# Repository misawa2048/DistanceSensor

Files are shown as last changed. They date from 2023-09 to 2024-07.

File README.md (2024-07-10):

# Open Distance Sensor 
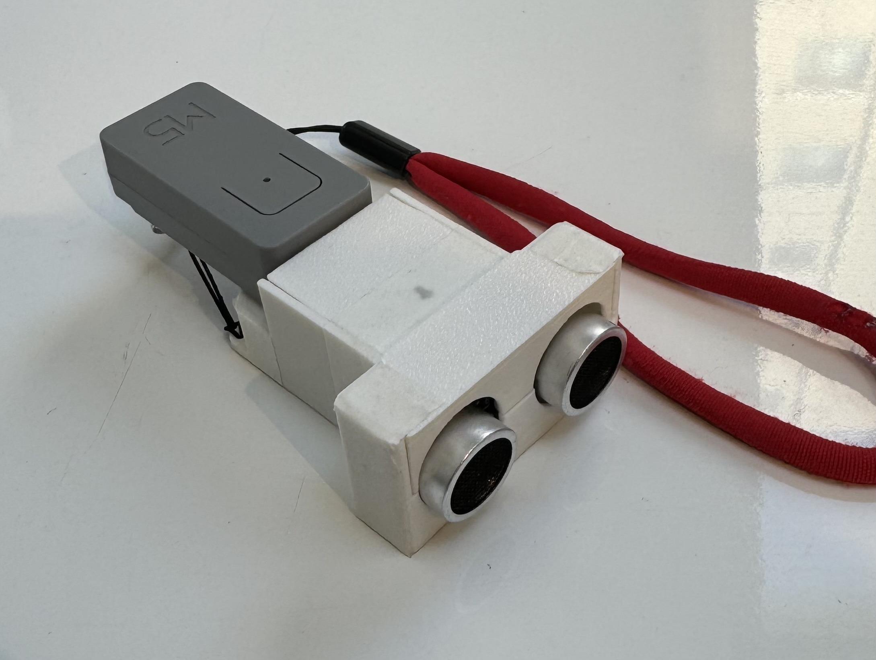
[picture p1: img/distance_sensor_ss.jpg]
  
Open DistanceSensorは、広く一般に流通しているパーツを使用して構成された超音波距離センサーです。 
最大4メートル前方の障害物を認識し、振動の間隔で距離をユーザーに伝えます。  
オープンソースですので、ここにあるデータを用いてどなたでも作成・ご活用いただけます。  

Open DistanceSensor is an ultrasonic distance sensor composed of widely available parts.  
It recognizes obstacles up to 4 meters ahead and tells the user the distance in terms of vibration intervals.  
Open source: Anyone can build and utilize it using the data available here.  

Distance sensor for the visually impaired  
https://youtube.com/shorts/7CfSE-uf2CA?si=v9oYDg3hjXETH1KF  
## Hardware
### PCB  
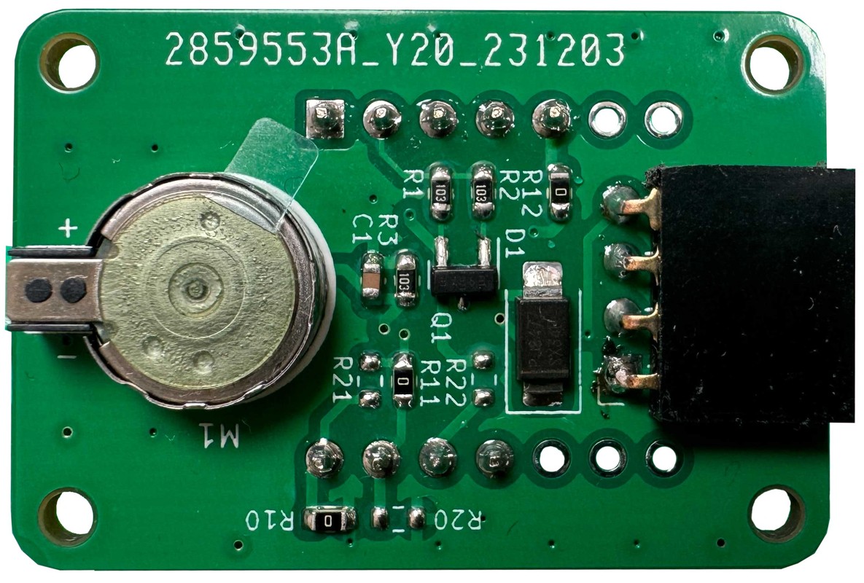
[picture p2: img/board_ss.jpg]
Printed circuit board
  

### STL
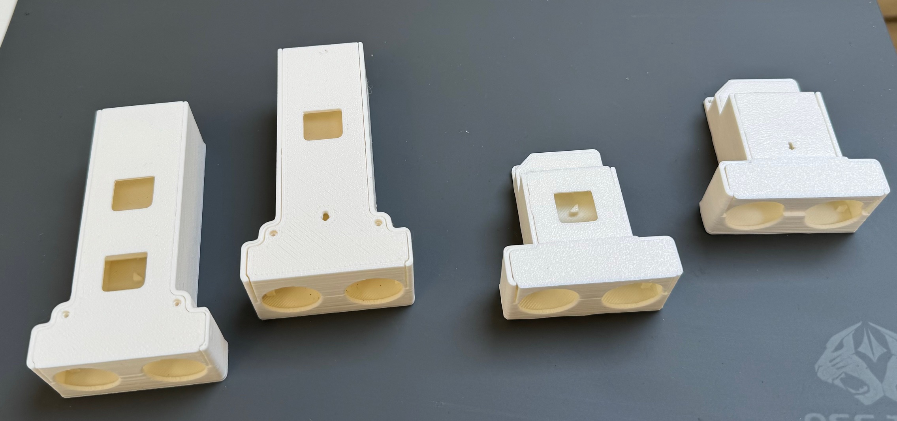
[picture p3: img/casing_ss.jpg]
3D print model
  

### pin asign  
XIAO_RP2040 (front side of mounting)  
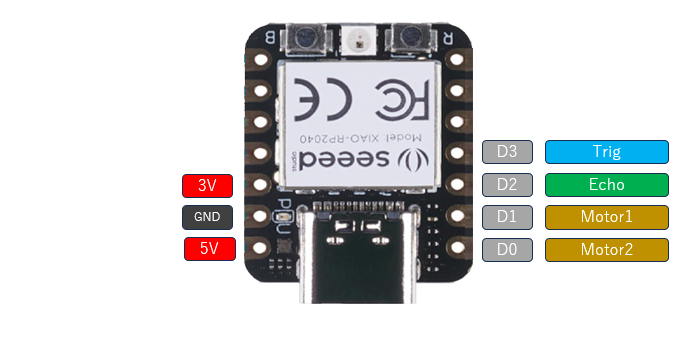
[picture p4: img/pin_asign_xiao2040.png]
pin asign
   
XIAO_RP2040 (front side of mounting)  
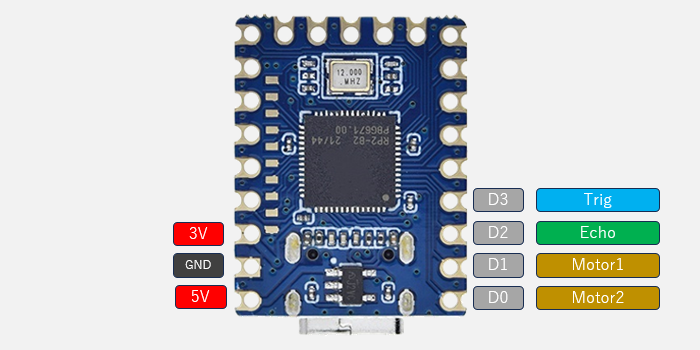
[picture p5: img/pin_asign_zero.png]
pin asign
   
ATOM_S3LITE (back side of mounting)    
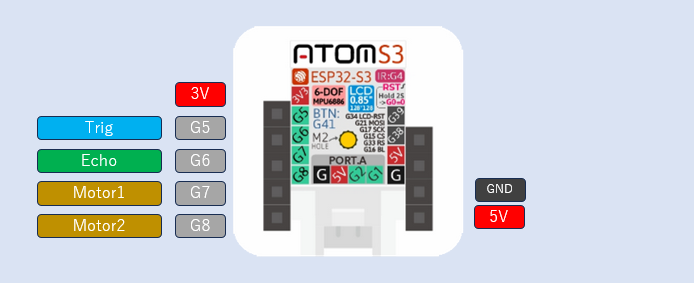
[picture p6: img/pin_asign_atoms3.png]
pin asign
   
 
## Software
Arduino IDE  
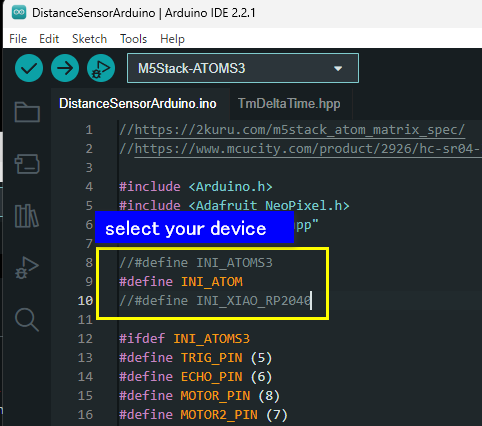
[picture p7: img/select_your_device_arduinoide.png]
select your device
  
PlatformIO  
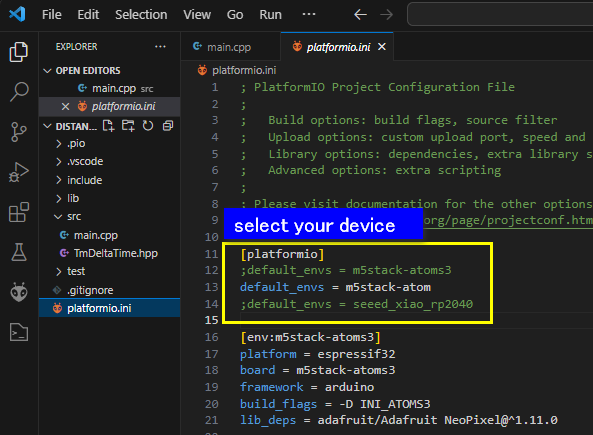
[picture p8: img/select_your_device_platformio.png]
select your device
  

### prototypes  
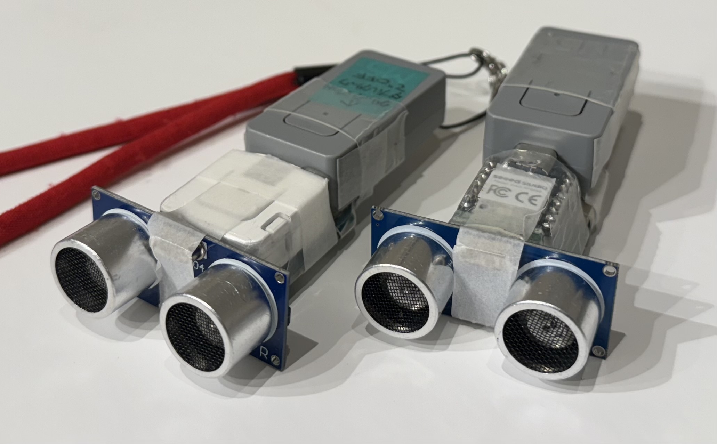
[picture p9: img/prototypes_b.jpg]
prototype
  
prototype  

## Support
こちらのプロジェクトは  
令和5年度 競争力強化支援事業（ソフトウェア開発費助成）として  
品川区より支援を受けております（支援金額:￥273000）。  

## Links  
[board manager settings](https://2kuru.com/m5stack_atom_matrix_spec/)  
[About distance sensor](https://www.mcucity.com/product/2926/hc-sr04-3-3v-5v-ultrasonic-distance-measuring-sensor-module-trig-echo-uarttx-rx-i2csdascl)

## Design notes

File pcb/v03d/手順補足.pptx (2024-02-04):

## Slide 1

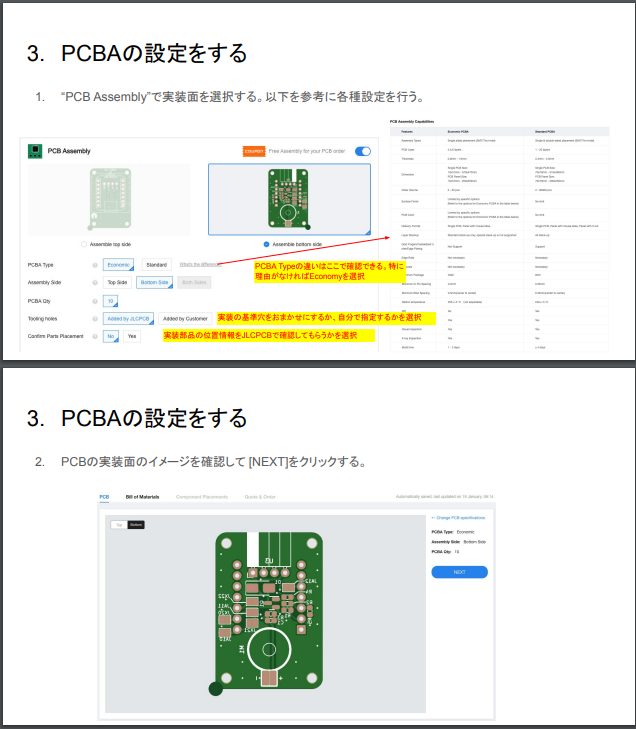
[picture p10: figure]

Calculated Priceの下にある[NEXT]を押す
を追加

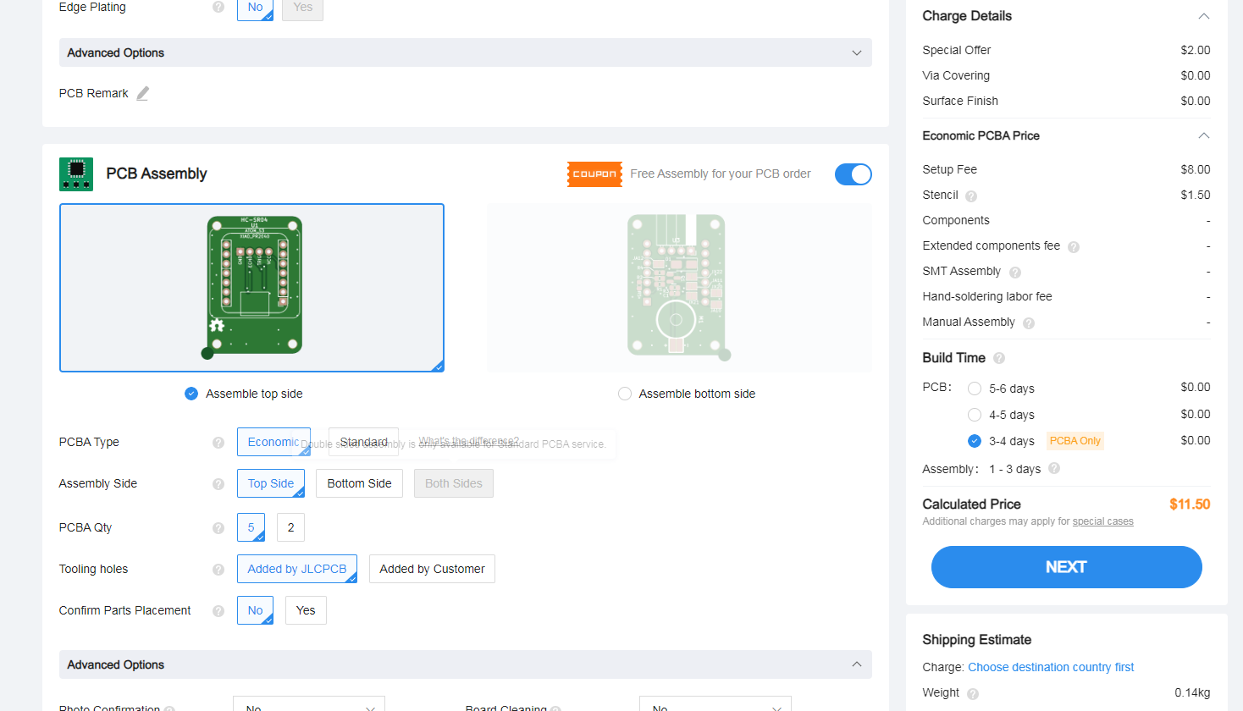
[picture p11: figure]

間に挟む

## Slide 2

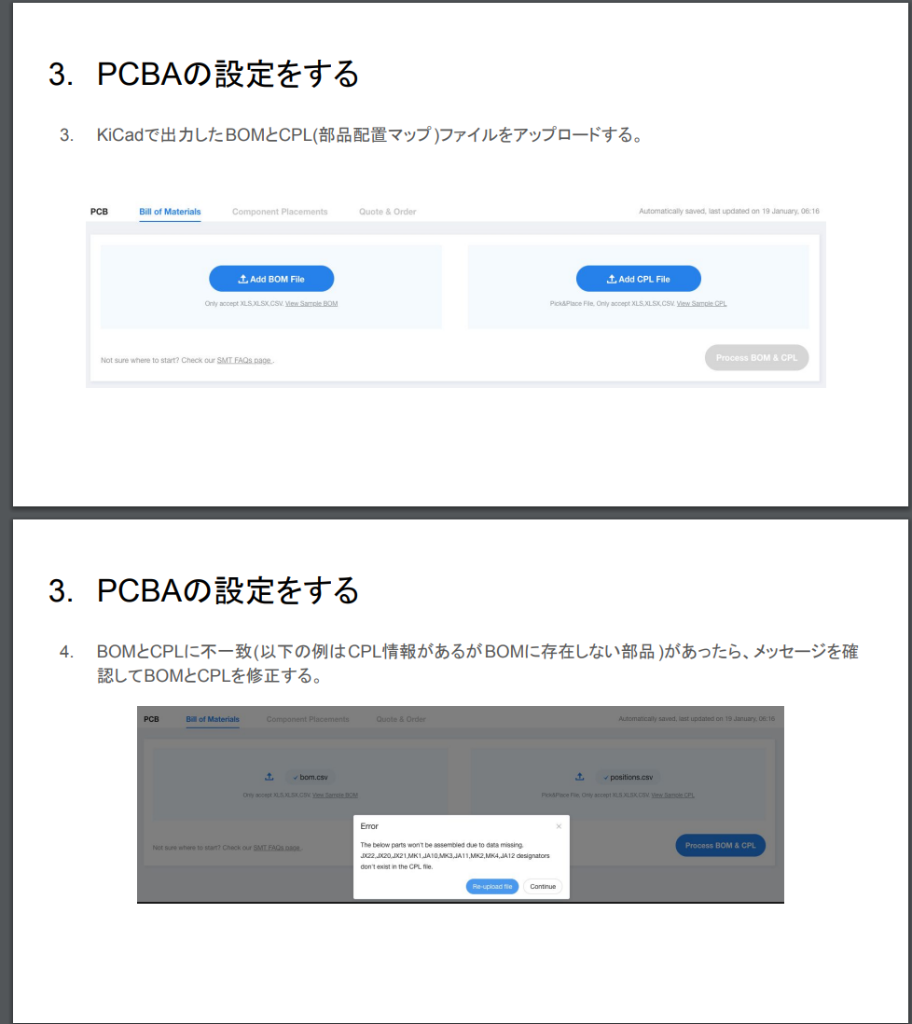
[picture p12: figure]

アップロード後の状態を追加
[Process BOM & CPL]を押す を追加

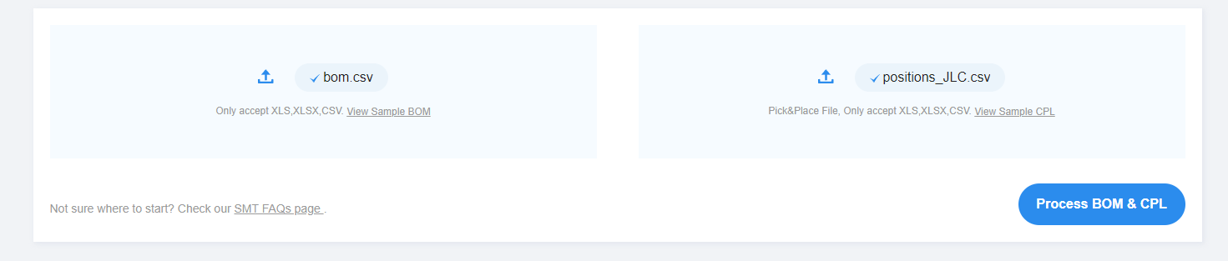
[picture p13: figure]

間に挟む

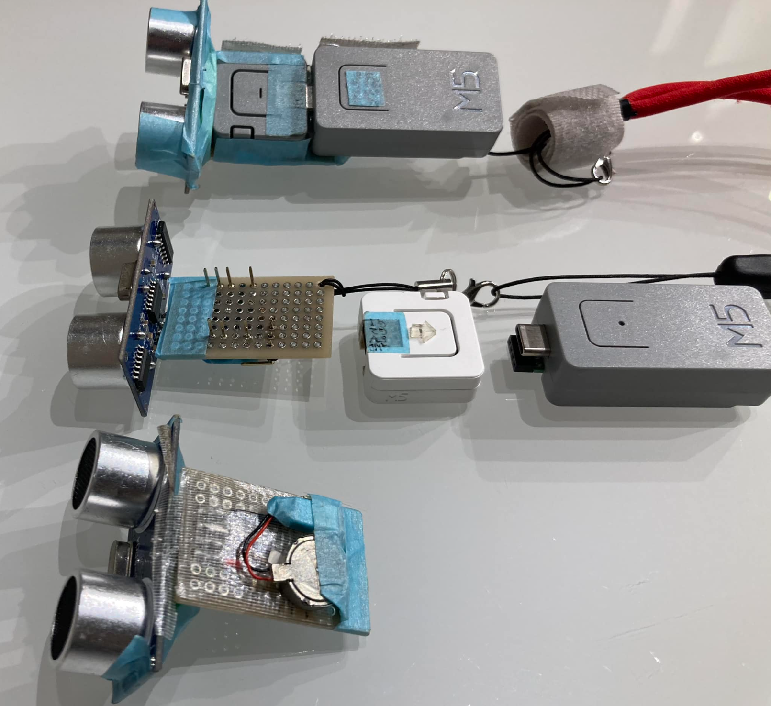
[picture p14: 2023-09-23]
img/prototype.png

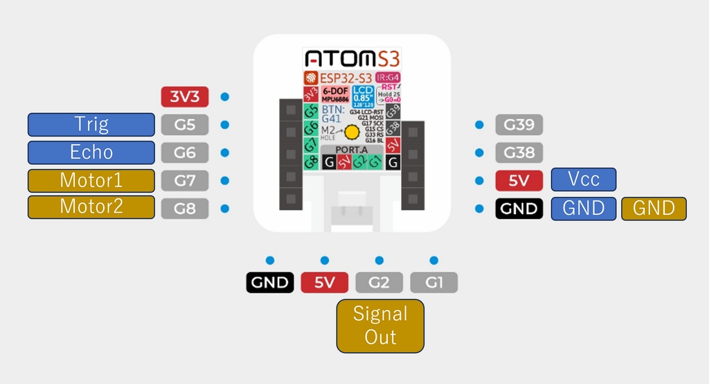
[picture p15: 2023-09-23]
img/pin_asign_DistanceSensor.png

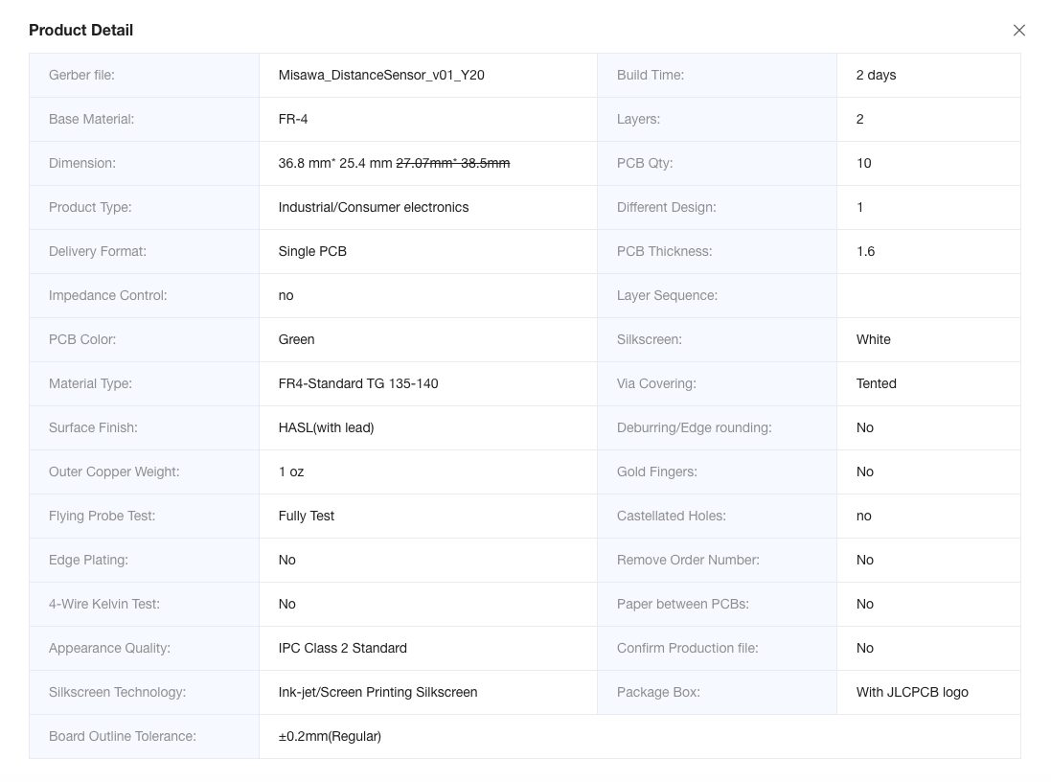
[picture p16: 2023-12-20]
pcb/detail.png

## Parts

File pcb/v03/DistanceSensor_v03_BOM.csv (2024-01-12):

Comment | Designator | Footprint | num | url
10K | R1,R2,R3 | R_0603_1608Metric | 3 | https://www.sengoku.co.jp/mod/sgk_cart/detail.php?code=EEHD-57GX
1K | R4 | R_0603_1608Metric | 1 | https://akizukidenshi.com/catalog/g/gR-11790/
1.5K | R5 | R_0603_1608Metric | 1 | https://www.sengoku.co.jp/mod/sgk_cart/detail.php?code=EEHD-57GL
0.1u | C1 | C_0603_1608Metric | 1 | https://akizukidenshi.com/catalog/g/gP-16143/
SX34F | D1 | D_SMA | 1 | https://akizukidenshi.com/catalog/g/gI-06124/
SOT-23 | Q1 | IRLML6402 | 1 | https://akizukidenshi.com/catalog/g/gI-02553/
PinSocket | U3 | 2802-L4 | 1 | https://eleshop.jp/shop/g/gE2H365/
Vibration Motor | M1 | LBV10B-009 | 1 | https://akizukidenshi.com/catalog/g/gP-06787/

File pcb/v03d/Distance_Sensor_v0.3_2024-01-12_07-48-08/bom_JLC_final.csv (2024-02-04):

Comment | Designator | Footprint | JLCPCB Part #
SS34F | D1 | D_SMA | C60396
0.1u | C1 | 603 | C14663
10k | R1,R2,R3 | 603 | C25804
IRLML6402 | Q1 | SOT-23 | C347504
1k | R4 | 603 | C21190
1.5k | R5 | 603 | C103309

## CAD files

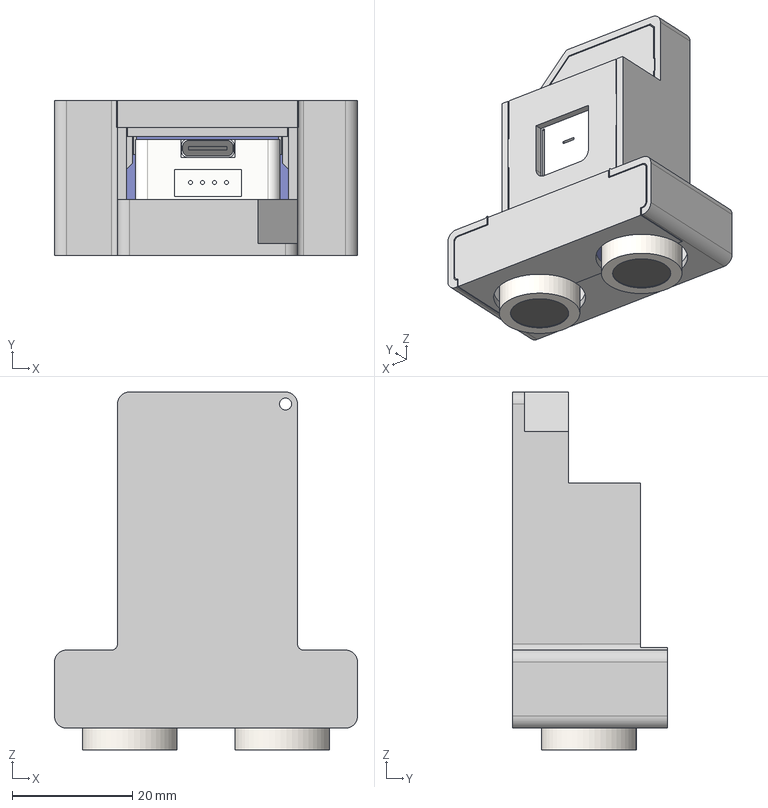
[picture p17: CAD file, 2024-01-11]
stl/ATOM/CASE_ATOM_v01.step
50.5 x 25.9 x 59.6 mm
Misawa_DistanceSensor PCB
Vib_Motor
Crystal
sp x 2
PCB
con1x4 x 2
socket1x4L
con1x5
Type-C

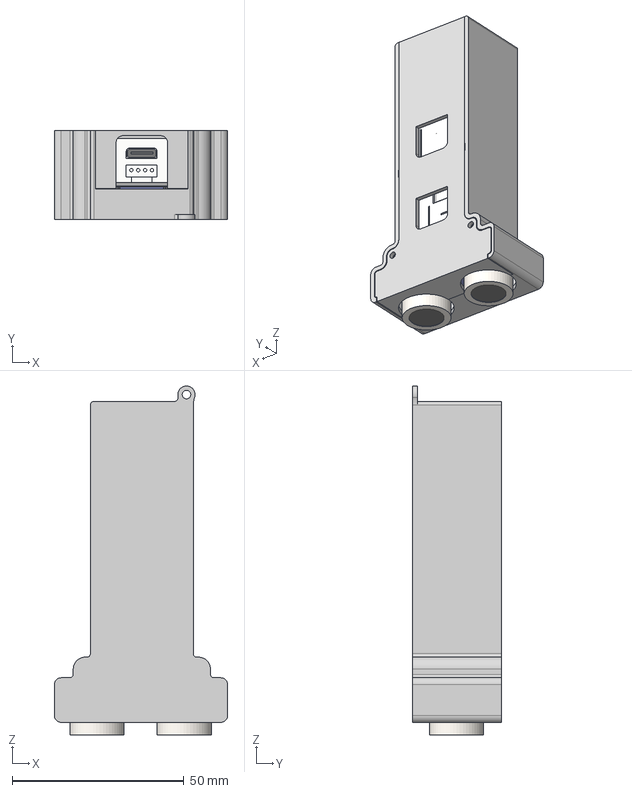
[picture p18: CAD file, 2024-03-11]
stl/ATOM/v04/CASE_ATOM_v04.step
50.5 x 25.9 x 101.7 mm
Type-C_Receptacle
Type-C_Plug
Grove_Socket
Misawa_DistanceSensor PCB
Crystal
sp x 2
PCB
con1x4 x 2
socket1x4L
con1x5
Type-C
LA3R5-480

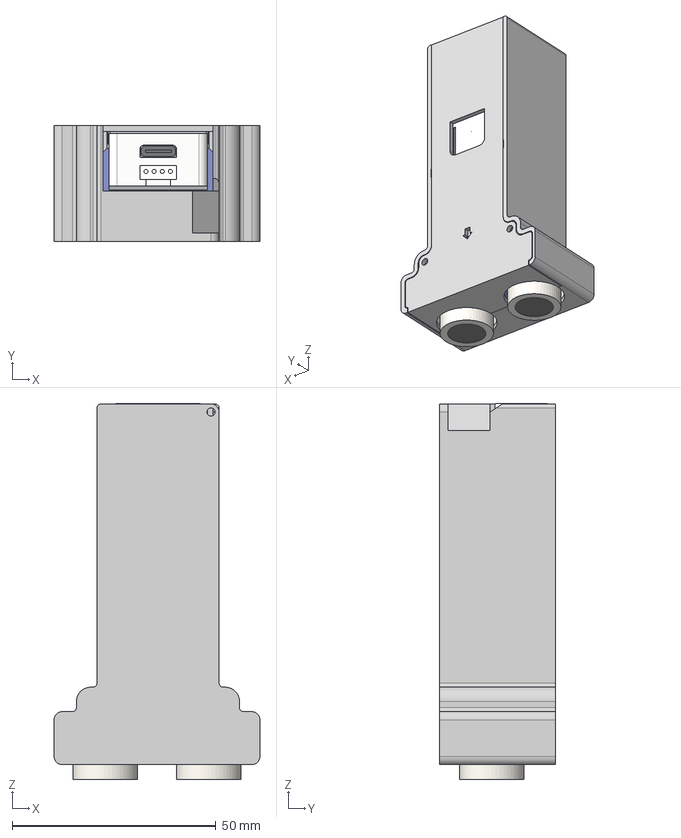
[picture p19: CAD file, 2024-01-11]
stl/XIAO/CASE_XIAO2040_v02.step
50.5 x 28.4 x 92.2 mm
Misawa_DistanceSensor PCB
Vib_Motor
Crystal
sp x 2
PCB
con1x4
socket1x7 x 2
PR2040
SW x 2
LED
Type-C
PCB_1
con1x7 x 2
socket1x4L
Type-C_Receptacle
Type-C_Plug
Grove_Socket

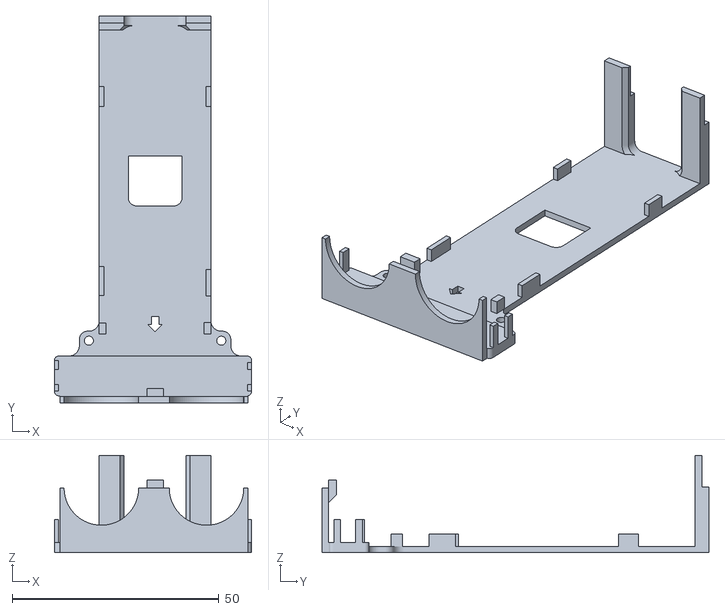
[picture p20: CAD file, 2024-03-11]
stl/XIAO/v04/case_top_2.stl
47.6 x 93.4 x 23.5

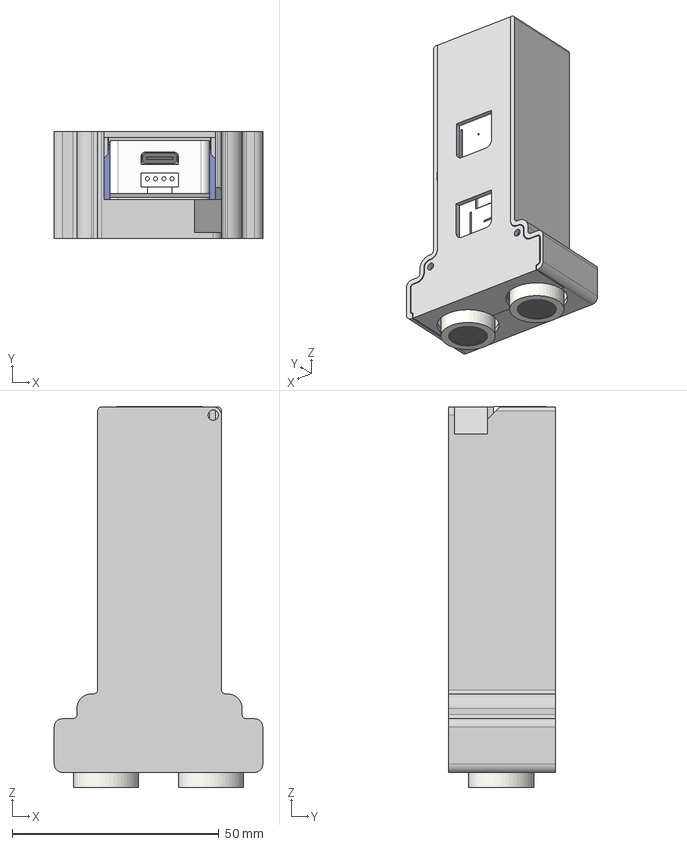
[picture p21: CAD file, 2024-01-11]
stl/ATOM/CASE_ATOM_v02.step
50.5 x 25.9 x 92.2 mm
Misawa_DistanceSensor PCB
Vib_Motor
Crystal
sp x 2
PCB
con1x4 x 2
socket1x4L
con1x5
Type-C
Type-C_Receptacle
Type-C_Plug
Grove_Socket

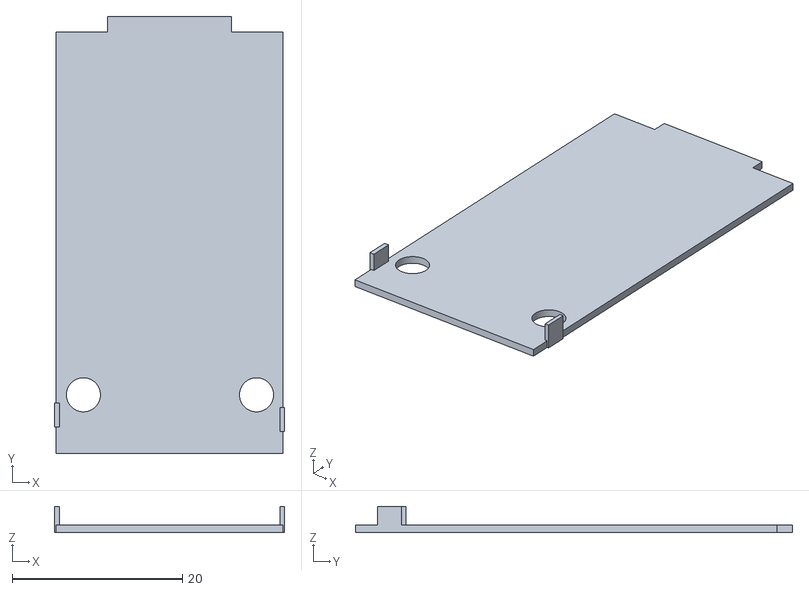
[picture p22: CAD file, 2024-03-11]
stl/ATOM/v04/case_top_3.stl
27.0 x 51.3 x 3.10

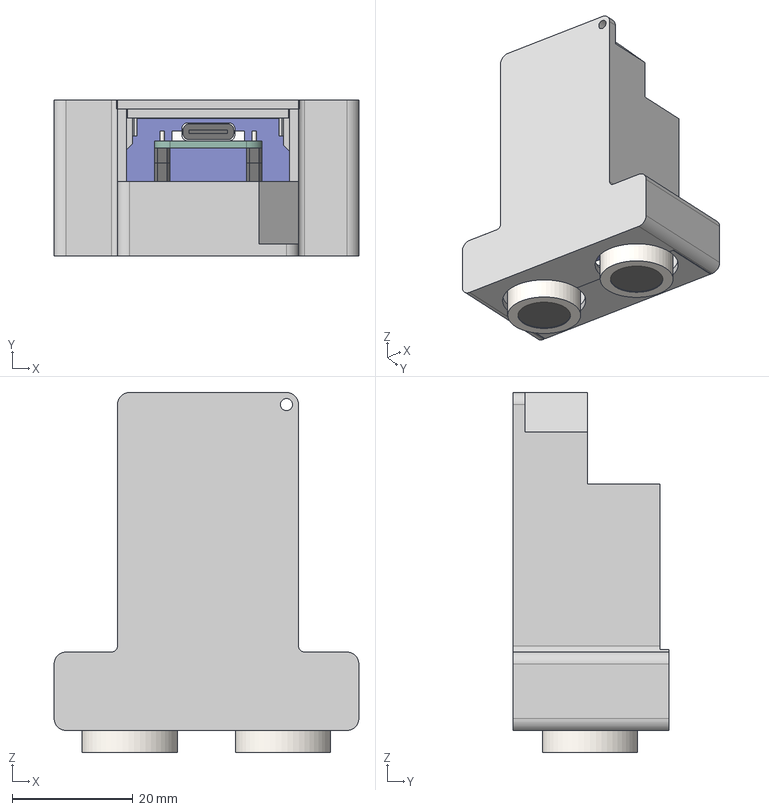
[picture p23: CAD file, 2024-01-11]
stl/XIAO/CASE_XIAO2040_v01.step
50.5 x 25.9 x 59.6 mm
Vib_Motor
Crystal
sp x 2
PCB
con1x4
socket1x7 x 2
PR2040
SW x 2
LED
Type-C
PCB_1
con1x7 x 2
socket1x4L

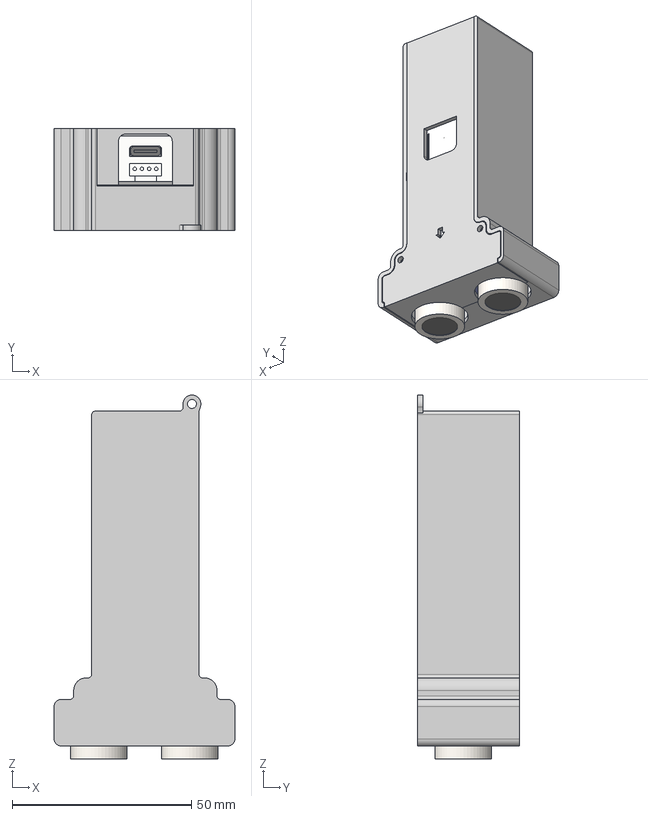
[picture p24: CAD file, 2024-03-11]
stl/XIAO/v04/CASE_XIAO2040_v04.step
50.5 x 28.4 x 101.6 mm
Type-C_Receptacle
Type-C_Plug
Grove_Socket
Misawa_DistanceSensor PCB
Crystal
sp x 2
PCB
con1x4
socket1x7 x 2
PR2040
SW x 2
LED
Type-C
PCB_1
con1x7 x 2
socket1x4L
LA3R5-480

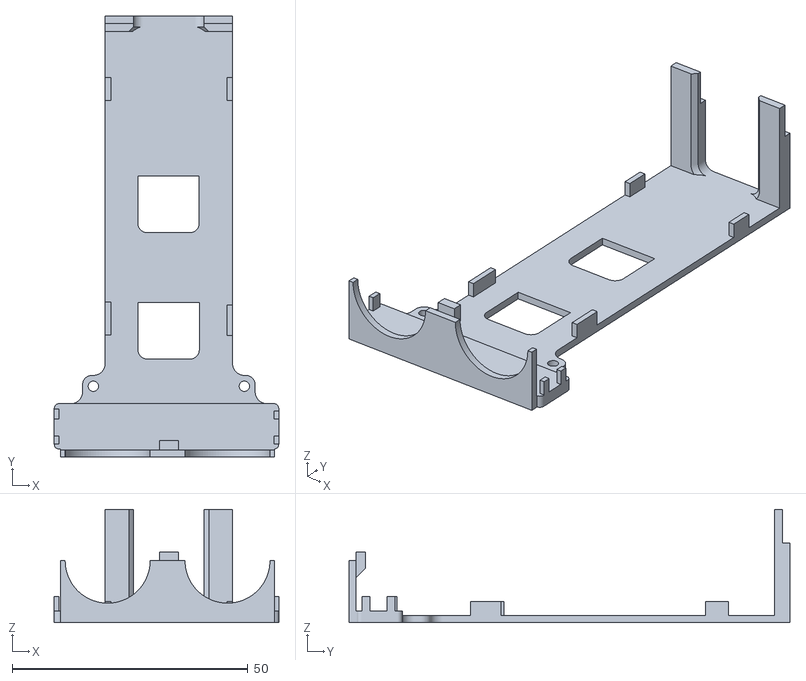
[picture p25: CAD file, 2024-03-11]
stl/ATOM/v04/case_top_2.stl
47.6 x 93.5 x 24.0

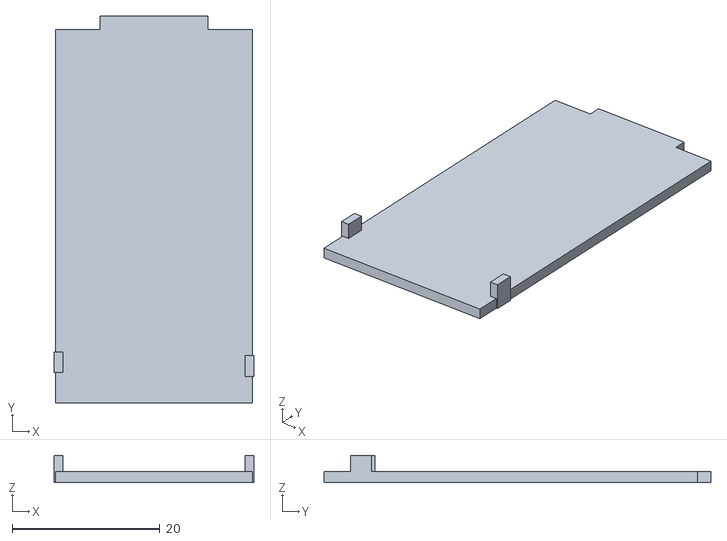
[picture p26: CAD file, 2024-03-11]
stl/XIAO/v04/case_top_3.stl
27.0 x 52.3 x 3.70

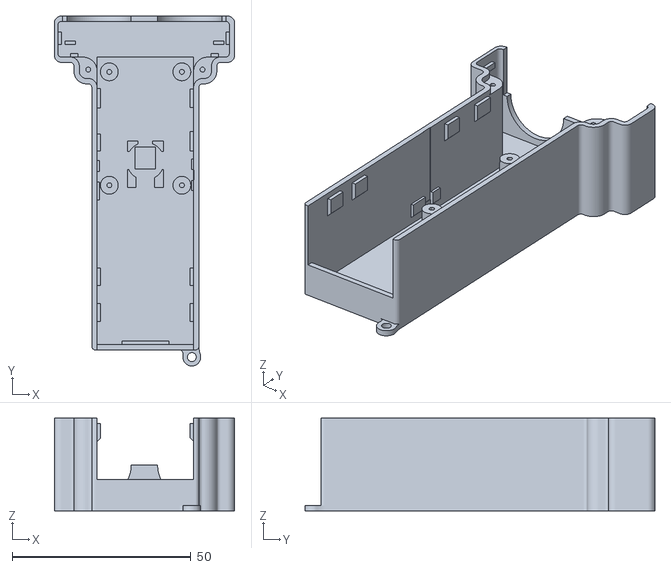
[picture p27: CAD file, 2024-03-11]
stl/ATOM/v04/case_bottom.stl
50.5 x 98.0 x 25.9

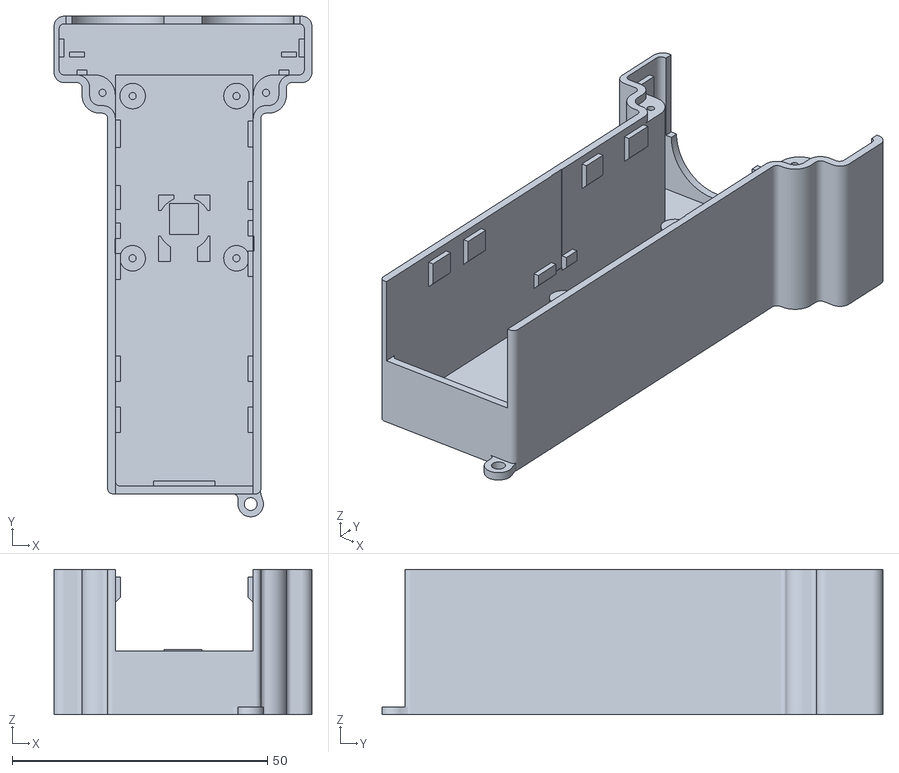
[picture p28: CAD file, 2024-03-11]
stl/XIAO/v04/case_bottom.stl
50.5 x 98.0 x 28.4

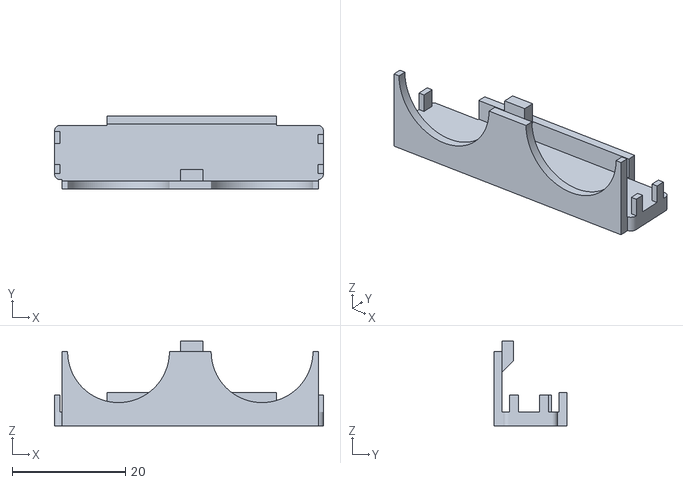
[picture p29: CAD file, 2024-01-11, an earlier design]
stl/ATOM/v01/case_top_1.stl
47.6 x 13.0 x 15.0

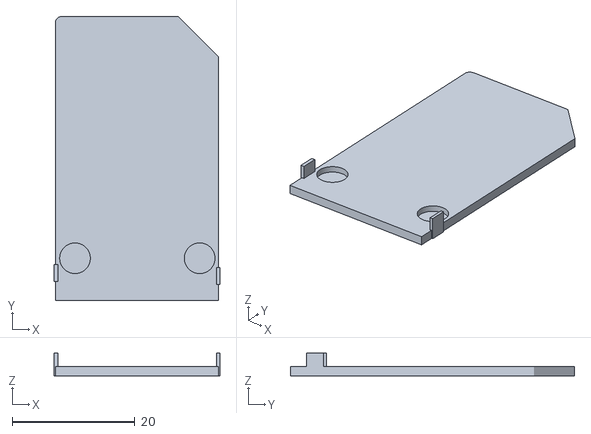
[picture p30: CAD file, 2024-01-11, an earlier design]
stl/ATOM/v02/case_top_3.stl
27.0 x 46.3 x 3.70

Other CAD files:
stl/XIAO/v01/case_top_1.stl
stl/XIAO/v02/case_top_3.stl
stl/ATOM/v01/case_top_2.stl
stl/ATOM/v02/case_bottom.stl
stl/ATOM/v01/case_bottom.stl
stl/ATOM/v01/case_top_3.stl
stl/ATOM/v02/case_top_2.stl
stl/XIAO/v01/case_bottom.stl
stl/XIAO/v01/case_top_2.stl
stl/XIAO/v01/case_top_3.stl
stl/XIAO/v02/case_bottom.stl
stl/XIAO/v02/case_top_2.stl

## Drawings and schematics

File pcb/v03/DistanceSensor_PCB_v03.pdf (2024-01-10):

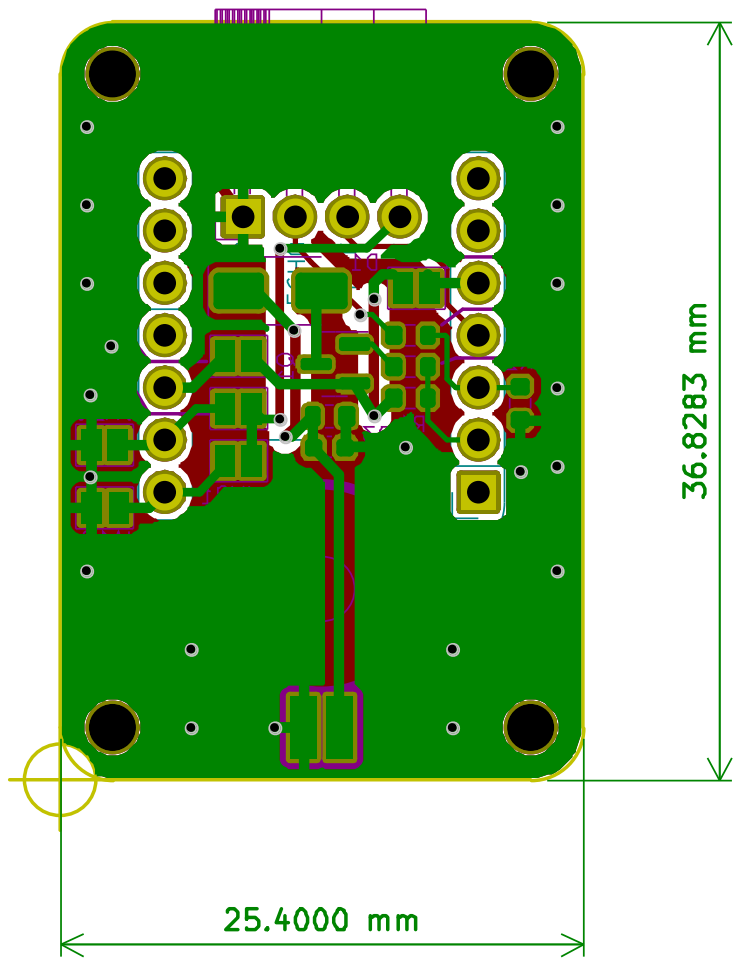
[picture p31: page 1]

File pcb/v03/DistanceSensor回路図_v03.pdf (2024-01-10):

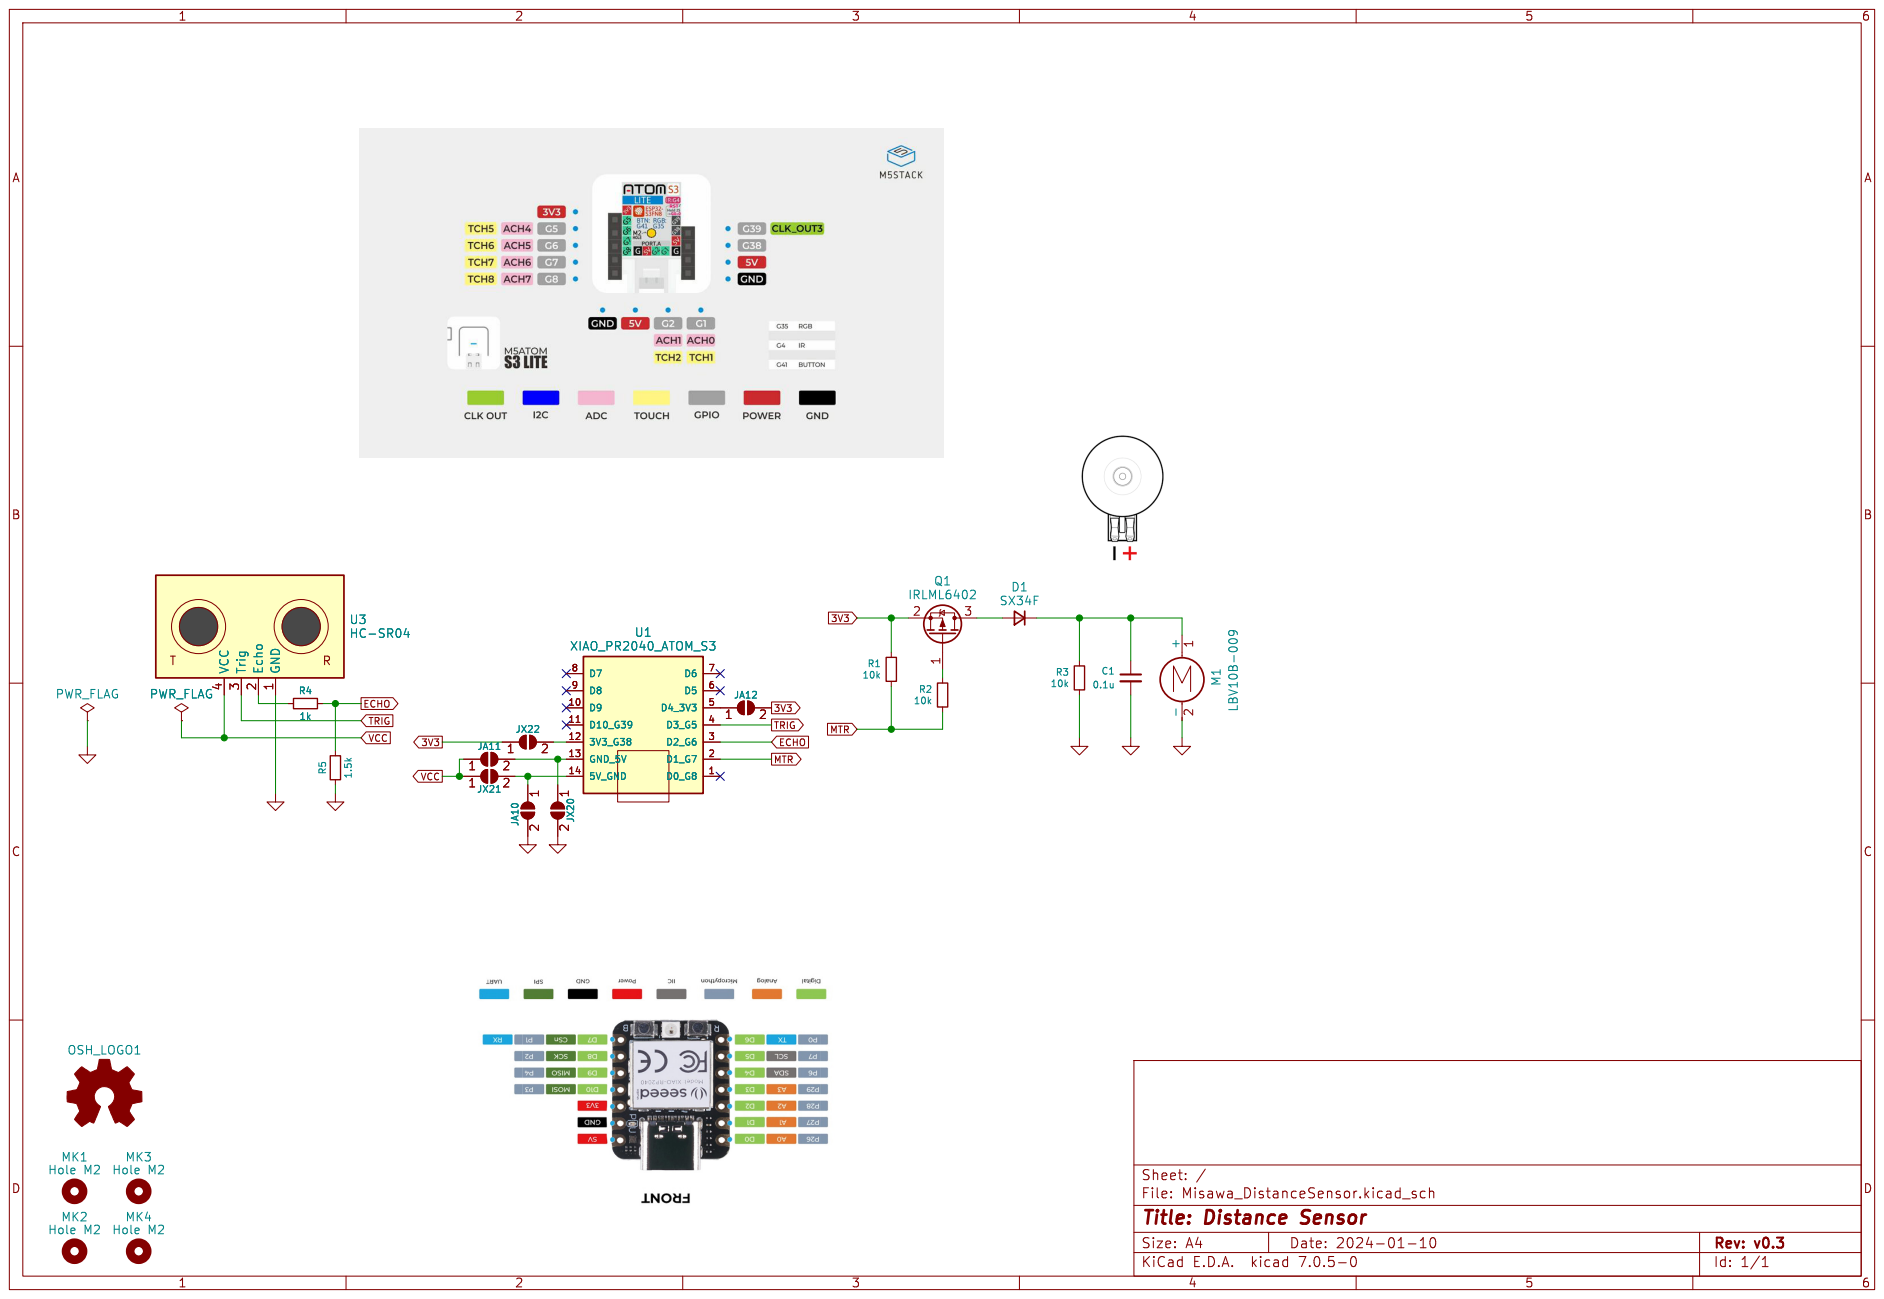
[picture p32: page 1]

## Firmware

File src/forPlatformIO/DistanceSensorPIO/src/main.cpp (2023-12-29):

#include <Arduino.h>
#include <Adafruit_NeoPixel.h>
#include "tmDeltaTime.hpp"

#ifdef INI_ATOMS3
#define TRIG_PIN (5)
#define ECHO_PIN (6)
#define MOTOR_PIN (8)
#define MOTOR2_PIN (7)
#define OUT_PIN (2)
#define NEO_PWR (16)
#define NEOPIX (35)
#define MOTOT_ON_STATE (LOW)
#endif
#ifdef INI_ATOM
#define TRIG_PIN (22)
#define ECHO_PIN (19)
#define MOTOR_PIN (33)
#define MOTOR2_PIN (23)
#define OUT_PIN (26)
#define NEO_PWR (26)
#define NEOPIX (27)
#define MOTOT_ON_STATE (LOW)
#endif
#ifdef INI_XIAO_RP2040
#define TRIG_PIN (D3)
#define ECHO_PIN (D2)
#define MOTOR_PIN (D1)
#define MOTOR2_PIN (D0)
#define OUT_PIN (D10)
#define NEO_PWR (11)
#define NEOPIX (12)
#define MOTOT_ON_STATE (LOW)
#endif
#ifdef INI_XIAO
#define TRIG_PIN (D3)
#define ECHO_PIN (D2)
#define MOTOR_PIN (D1)
#define MOTOR2_PIN (D0)
#define OUT_PIN (D10)
#define NEO_PWR (11)
#define NEOPIX (12)
#define MOTOT_ON_STATE (LOW)
#endif
#ifdef INI_RP2040_ZERO
#define TRIG_PIN (3)
#define ECHO_PIN (2)
#define MOTOR_PIN (1)
#define MOTOR2_PIN (0)
#define OUT_PIN (10)
#define NEO_PWR (16)
#define NEOPIX (16)
#define MOTOT_ON_STATE (LOW)
#endif

#define USE_SERIAL false
#define NUMPIXELS 1
Adafruit_NeoPixel pixels(NUMPIXELS, NEOPIX, NEO_GRB + NEO_KHZ800);

#define MAX_DIST_MM (4000)
#define TIMEOUT_USEC (100000)
#define TRIG_USEC (20)
#define DIST_INTERVAL_MSEC (150)
#define MOTOR_INTERVAL_MSEC (30)
#define HEARTBEAT_INTERVAL_MSEC (4000)

int32_t g_dist_mm;
int32_t g_mtTime;
bool g_mtIsOn;
bool g_mtCancelHeartbeat;
TmDeltaTime* pTdt= new TmDeltaTime();

void updateDist(uint32_t deltaTime){
  digitalWrite(TRIG_PIN,HIGH);
  delayMicroseconds(TRIG_USEC);
  digitalWrite(TRIG_PIN,LOW); // Trig pin outputs 10US high level pulse trigger signal

  unsigned long dist = pulseIn(ECHO_PIN,HIGH,TIMEOUT_USEC); // Count the received high time
  g_dist_mm = (dist==0) ? MAX_DIST_MM : (int32_t)(dist*340/2/1000); // Calculation distance
  #if USE_SERIAL
  Serial.println(g_dist_mm); // Serial port output distance signal
  #endif
}

void updateMotorPin(bool isOn){
  bool isOnState = (MOTOT_ON_STATE==HIGH)?isOn:!isOn;
  digitalWrite(MOTOR_PIN,isOnState);
  digitalWrite(MOTOR2_PIN,isOnState);
  digitalWrite(OUT_PIN,isOnState);
  if(isOn){
    pixels.setPixelColor(0, pixels.Color(0, 55, 0));
  }else{
    pixels.setPixelColor(0, pixels.Color(0, 0, 0));
  }
  pixels.show();
}

void updateMotor(uint32_t deltaTime){
  if(!g_mtIsOn){
    if(g_dist_mm>=MAX_DIST_MM){
      return;
    }
    if(g_dist_mm<g_mtTime){
      g_mtTime=g_dist_mm;
    }
    g_mtTime -= deltaTime;
    //Serial.println(g_mtIsOn?"++":"--");
    if(g_mtTime<0){
      g_mtIsOn=!g_mtIsOn;
      updateMotorPin(g_mtIsOn);
      g_mtTime+= ((g_dist_mm>1500)?150:75);
      g_mtCancelHeartbeat=true;
    }
  }else{
    g_mtTime -= deltaTime;
    //Serial.println(g_mtIsOn?"++":"--");
    if(g_mtTime<0){
      g_mtIsOn=!g_mtIsOn;
      updateMotorPin(g_mtIsOn);
      g_mtTime+=(g_dist_mm>>2);
    }
  }
}

void updateHeartbeat(uint32_t deltaTime){
  if(!g_mtCancelHeartbeat){
    pixels.setPixelColor(0, pixels.Color(55, 0, 0));
    pixels.show();
    delay(10);
    pixels.setPixelColor(0, pixels.Color(0, 0, 0));
    pixels.show();
  }
  g_mtCancelHeartbeat=false;
}

void setup() {
  pinMode(NEO_PWR,OUTPUT);  digitalWrite(NEO_PWR, HIGH);
  pixels.begin();
  pixels.setBrightness(20);
  delay(100);

#if USE_SERIAL
  Serial.begin(115200);
  delay(10);
  Serial.println("Start");
#endif

  pinMode(ECHO_PIN,INPUT);
  pinMode(TRIG_PIN,OUTPUT);
  pinMode(MOTOR_PIN,OUTPUT);
  pinMode(MOTOR2_PIN,OUTPUT);
  pinMode(OUT_PIN,OUTPUT);
  digitalWrite(MOTOR_PIN,HIGH);
  g_dist_mm=0;
  g_mtTime=1000;
  g_mtIsOn=false;
  g_mtCancelHeartbeat=false;
  pTdt->Setup();
  pTdt->AddTrig(updateDist,DIST_INTERVAL_MSEC);
  pTdt->AddTrig(updateMotor,MOTOR_INTERVAL_MSEC);
  pTdt->AddTrig(updateHeartbeat,HEARTBEAT_INTERVAL_MSEC);
}

void loop() {
  pTdt->Update();
  delay(5);
}

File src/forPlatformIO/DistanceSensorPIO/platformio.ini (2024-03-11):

; PlatformIO Project Configuration File
;
;   Build options: build flags, source filter
;   Upload options: custom upload port, speed and extra flags
;   Library options: dependencies, extra library storages
;   Advanced options: extra scripting
;
; Please visit documentation for the other options and examples
; https://docs.platformio.org/page/projectconf.html

[platformio]
;default_envs = m5stack-atoms3
;default_envs = m5stack-atom
default_envs = seeed_xiao_rp2040
;default_envs = seeed_xiao
;default_envs = rp2040_zero

[env:m5stack-atoms3]
platform = espressif32
board = m5stack-atoms3
framework = arduino
build_flags = -D INI_ATOMS3 -D ARDUINO_USB_MODE=1 -D ARDUINO_USB_CDC_ON_BOOT=1    
lib_deps = adafruit/Adafruit NeoPixel@^1.11.0
monitor_speed = 115200

[env:m5stack-atom]
platform = espressif32
board = m5stack-atom
framework = arduino
build_flags = -D INI_ATOM
lib_deps = adafruit/Adafruit NeoPixel@^1.11.0
monitor_speed = 115200

[env:seeed_xiao_rp2040]
platform = https://github.com/maxgerhardt/platform-raspberrypi.git
board = seeed_xiao_rp2040
board_build.core = earlephilhower
board_build.filesystem_size = 0.5m
framework = arduino
build_flags = -D INI_XIAO_RP2040
lib_deps = adafruit/Adafruit NeoPixel@^1.11.0
monitor_speed = 115200

[env:seeed_xiao]
platform = atmelsam
board = seeed_xiao
framework = arduino
build_flags = -D INI_XIAO
lib_deps = adafruit/Adafruit NeoPixel@^1.11.0
monitor_speed = 115200

[env:rp2040_zero]
platform = https://github.com/maxgerhardt/platform-raspberrypi.git
board = seeed_xiao_rp2040
board_build.core = earlephilhower
board_build.filesystem_size = 0.5m
framework = arduino
build_flags = -D INI_RP2040_ZERO
lib_deps = adafruit/Adafruit NeoPixel@^1.11.0
monitor_speed = 115200

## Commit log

2023-09-23 Update Arduino IDE source code to be the same as PlatformIO
2023-09-24 relocate pin assign of XIAO 2040
2023-11-13 For XIAO, motor spins in LOW level.
2023-12-19 motor spins in LOW level
2023-12-20 add PCB data
    [Misawa_DistanceSensor-B_Cu.gbl, Misawa_DistanceSensor-B_Mask.gbs, Misawa_DistanceSensor-B_Paste.gbp, Misawa_DistanceSensor-B_Silkscreen.gbo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]
2024-01-12 change BOM file from xlsx to csv
    [DistanceSensor_v03_BOM.csv, DistanceSensor_v03_BOM.xlsx]
2024-01-14 skip session key
    [DistanceSensor_v03_positions.csv, bom.csv, positions.csv]
2024-01-14 Revert "skip session key"
    This reverts commit 0e4378d5404684c692c650135b339f4030f244bf.
    [DistanceSensor_v03_positions.csv, bom.csv, positions.csv]
2024-02-04 upload pcb Ordering documents
    [bom.csv, bom.xls, designators.csv, positions_JLC.csv]
2024-03-11 Case ver04
    [CASE_ATOM_v04.step, CASE_XIAO2040_v04.step, bom_JLC_final.csv, bom_JLC_final.xls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]
